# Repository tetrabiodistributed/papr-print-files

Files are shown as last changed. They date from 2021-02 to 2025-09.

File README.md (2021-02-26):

# papr-print-files
This repository contains all of the files necessary to print components of the Tetra PAPR.

Please see the documentation in https://tetrabiodistributed.github.io/papra/.

Please note that there is no warranty, real or implied, for those who build these devices on their own.  We simply cannot assure the quality of the work you've done.

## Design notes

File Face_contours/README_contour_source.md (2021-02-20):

# Contour Sourcing
-----------------

These contours were derived using NIOSH headforms, referenced below.  Once the headform had been loaded into Fusion 360, the following procedure was used to create the contours:

Beginning with the NIOSH large 3D headform, the initial design was created on a 2D plane using a B-spline for the inner profile, relative to the headform not using any explicit geometric relations. The spline positioning and shape was adjusted to mimic the coverage of existing FFRs. A copy of the profile was then projected 4 mm radially outward in the same plane to create the outer profile. These two B-splines were joined with vertical lines at either end to create a closed contour. The contour was projected from the 2D plane onto the 3D surface of the Large NIOSH Headform from the Principal Component Analysis Study, forming the face contact surface. The surface was then mirrored about the center plane.

## Additional references
---------------------

1. "Advanced Headforms for Evaluating Respirator Fit", Michael Bergman, MS; Ziqing Zhuang, PhD; Ronald E. Shaffer, PhD . July 25, 2013. Referenced from https://blogs.cdc.gov/niosh-science-blog/2013/07/25/headforms/ on Feb 13, 2021.

2. "NIOSH Anthropometric Data and ISO Digital Headforms" Updated on Updated April 23, 2020. NIOSH Dataset RD-10130-2020-0. Referenced from https://www.cdc.gov/niosh/data/datasets/rd-10130-2020-0/default.html on Feb 13, 2021.

3. Zhuang, Z.Q., B. Bradtmiller, and R.E. Shaffer: New respirator fit test panels representing the current US civilian work force. Journal of Occupational and Environmental Hygiene 4(9): 647-659 (2007).

4. Zhuang, Z., S. Benson, and D. Viscusi: Digital 3-D headforms with facial features representative of the current US workforce. Ergonomics 53(5): 661-671 (2010).

5. Hanson, D., R. Bergs, Y. Tadesse, V. White, and S. Priya: Enhancement of EAP Actuated Facial Expressions by Designed Chamber Geometry in Elastomers. Proc. SPIE’s Electroactive Polymer Actuators and Devices Conf., 10th Smart Structures and Materials Symposium, San Diego(2006).

6. Hanson, D., and V. White: Converging the Capabilities of ElectroActive Polymer Artificial Muscles and the Requirements of Bio-inspired Robotics. Smart Structures and Materials 2004: Electroactive Polymer Actuators and Devices (EAPAD), edited by Yoseph Bar-Cohen, Proceedings of SPIE Vol. 5385 (SPIE, Bellingham, WA), 2004.

7. Bergman, M., Z. Zhuang, R.J. Wande, D. Hanson, B. Heimbuch, M. McDonald et al.: Development of an Advanced Respirator Fit Test Headform. Journal of Occupational and Environmental Hygiene In Press(2013).

8. Zhuang, Z., M. Bergman, M. Joseph, and R. Shaffe: Human Correlation Fit Testing of a Static Advanced Headform. Presentation at the NPPTL Stakeholder Meeting on Respiratory Protection for Healthcare Workers, Atlanta, GA June 18, 2013 (2013).

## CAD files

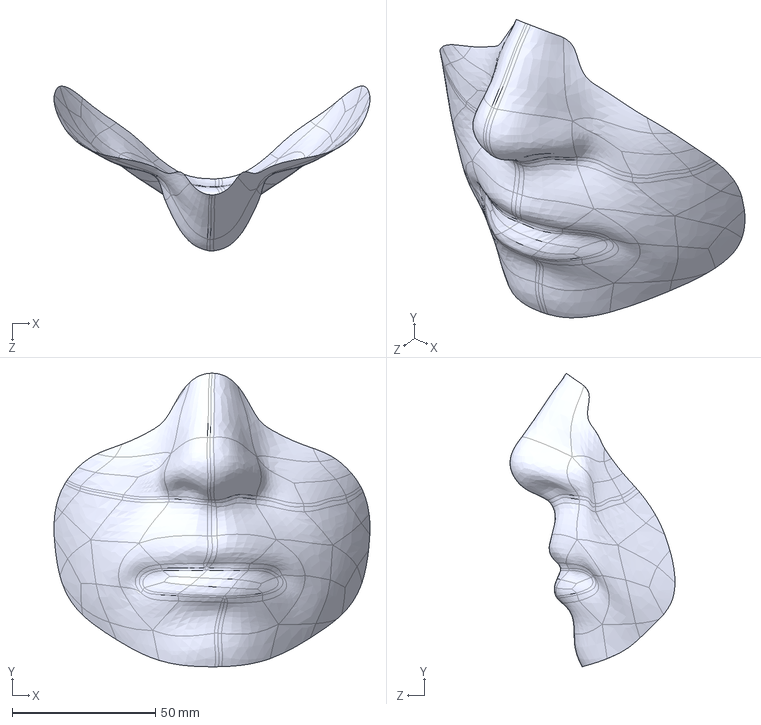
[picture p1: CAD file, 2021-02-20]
Face_contours/STEP/full_face/LRG_face_surface-full.STEP
110.4 x 102.5 x 57.6 mm

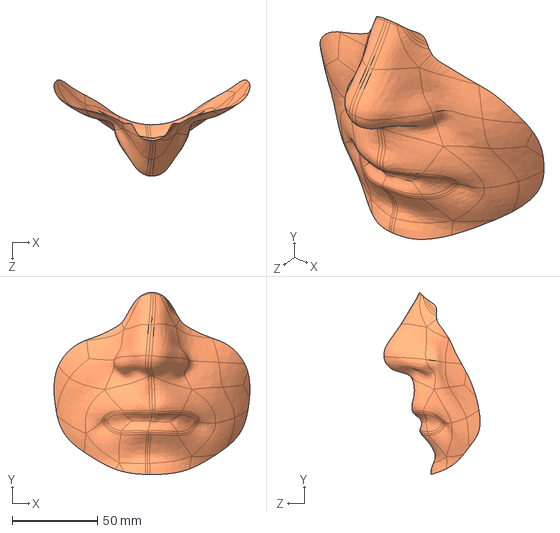
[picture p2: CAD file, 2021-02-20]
Face_contours/STEP/full_face/LRG_face_surface-full_5mm.STEP
115.0 x 106.8 x 56.5 mm

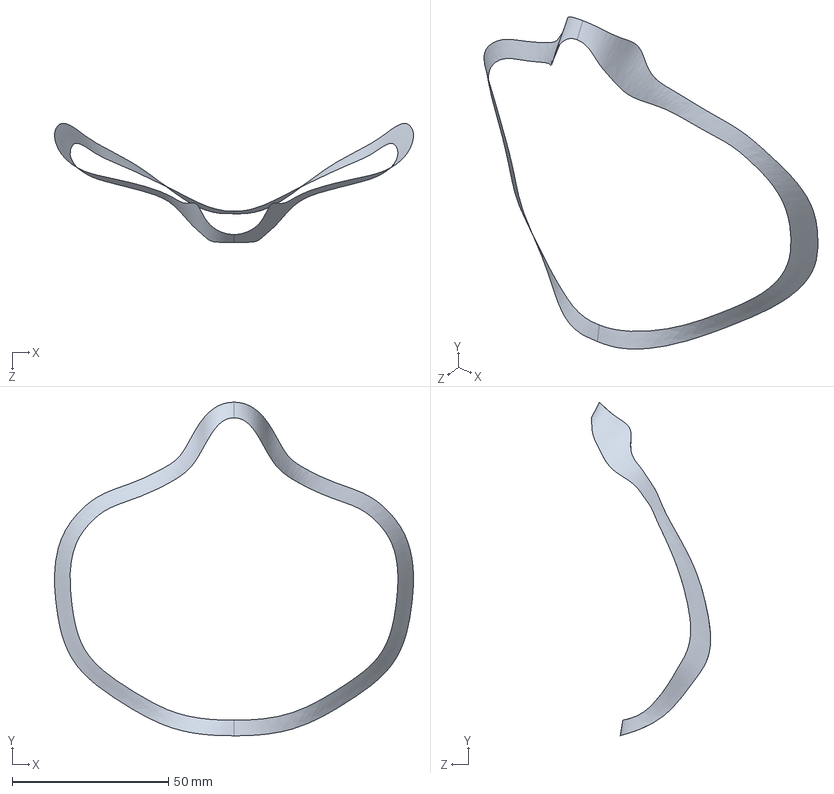
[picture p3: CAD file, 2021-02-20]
Face_contours/STEP/LRG_face_surface.STEP
114.9 x 106.8 x 38.2 mm

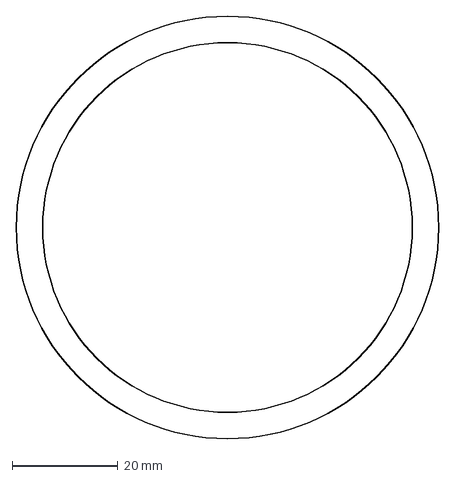
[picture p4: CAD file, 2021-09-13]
Gaskets/GermGuardian Filter PAPRa/P-TET-000121-1_Mask Gasket.dxf
80.0 x 80.0 mm

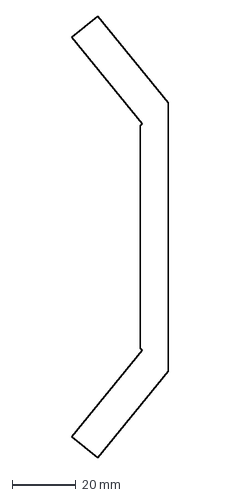
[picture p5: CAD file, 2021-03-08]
Gaskets/P-TET-000117-0 Funnel Gasket.dxf
30.2 x 138.2 mm

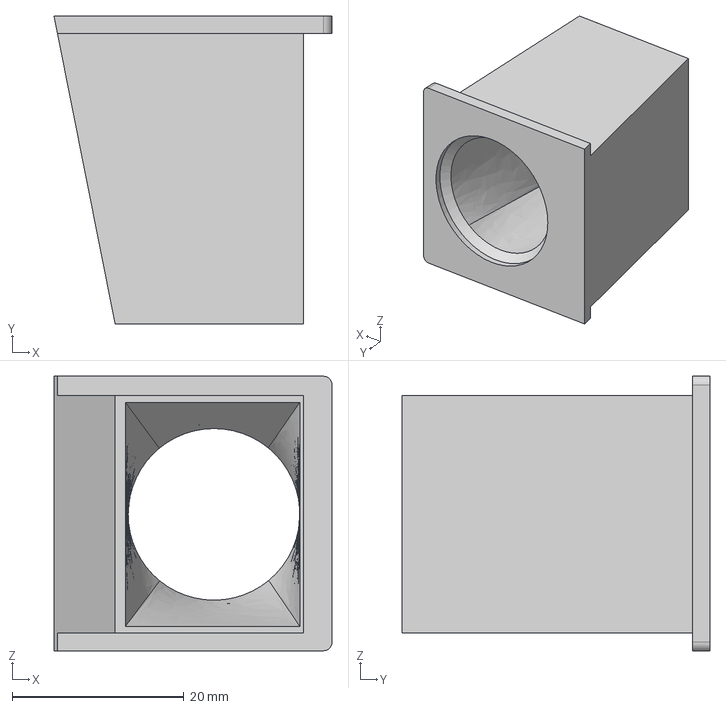
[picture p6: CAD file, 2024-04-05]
STEP/120mm Stealth Fan Box/P-TET-000179 Spout Interface.step
32.4 x 35.9 x 32.0 mm

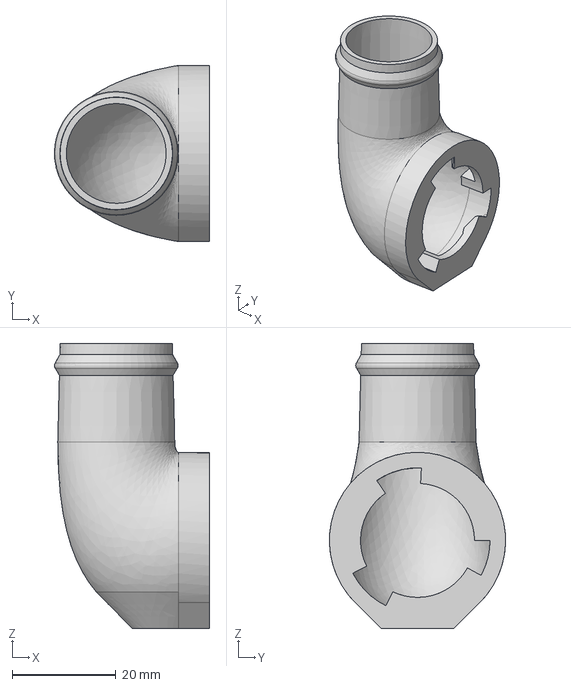
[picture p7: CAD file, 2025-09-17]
STEP/3M_Adapter/P-TET-000150 - 3M Right Angle Adapater.step
29.9 x 34.0 x 55.0 mm

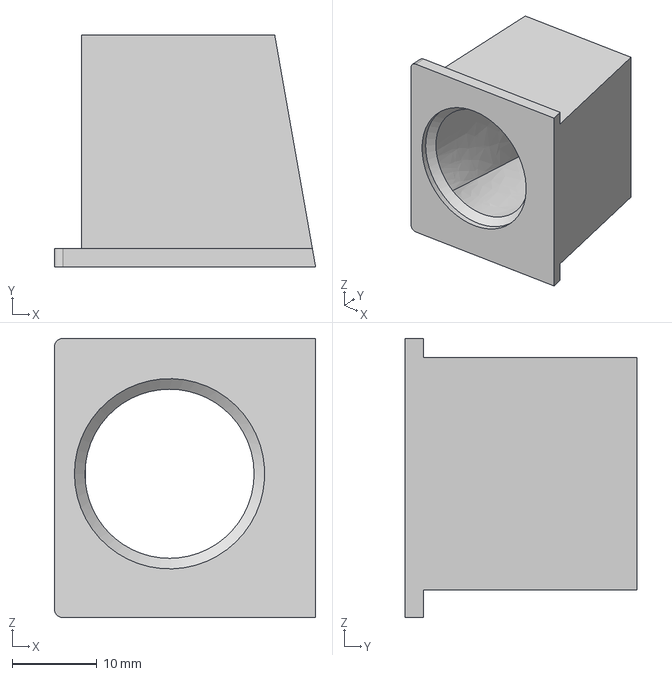
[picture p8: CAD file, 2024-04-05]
STEP/96mm Sanyo Fan Box/P-TET-000152 Spout Interface.step
30.9 x 27.5 x 33.0 mm

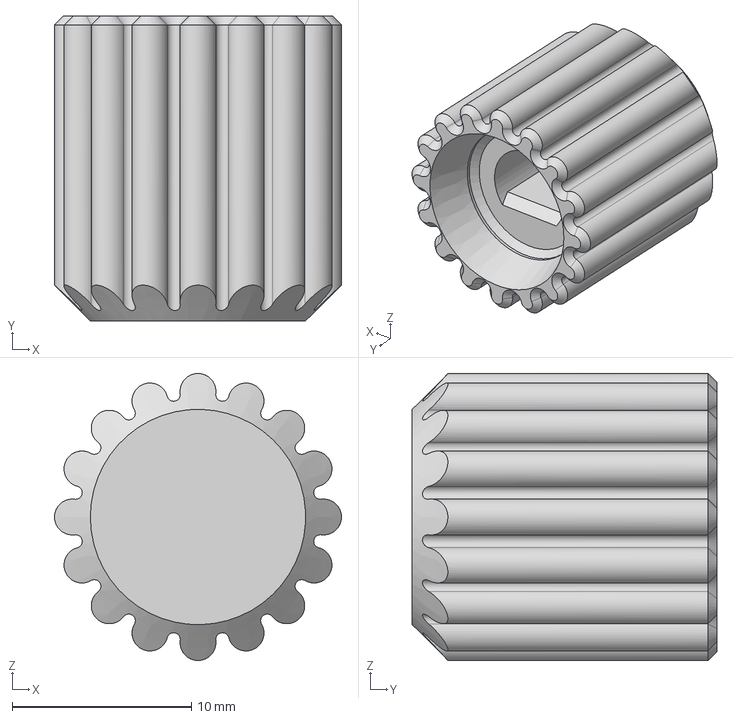
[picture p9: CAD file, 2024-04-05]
STEP/M12 Battery Housing/P-TET-000100 M12 Knob.step
16.0 x 17.0 x 16.0 mm

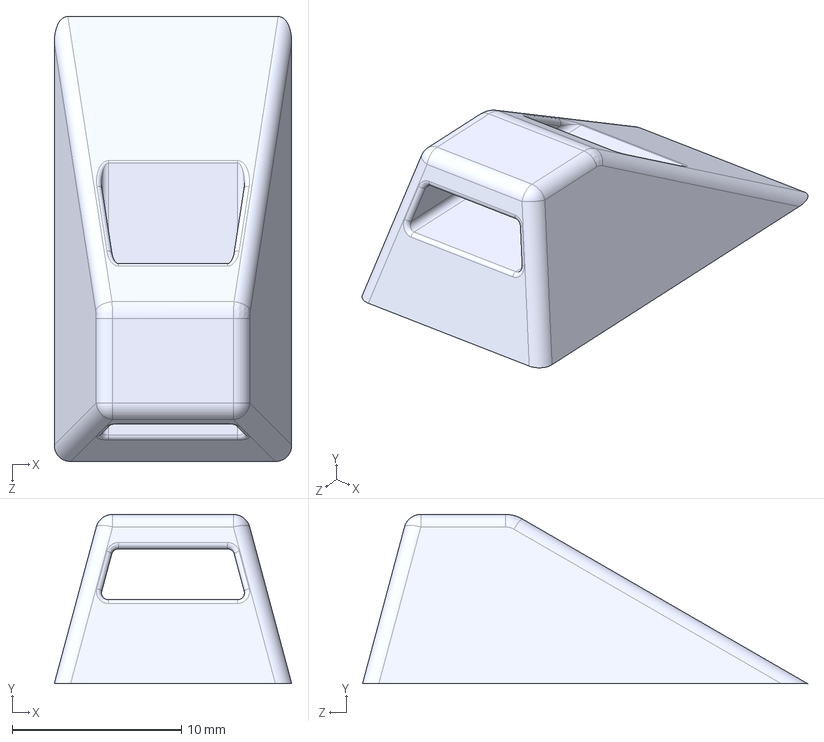
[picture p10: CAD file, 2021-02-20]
STEP/PAPR_strap_mounts/PAPR_facefit_strap_tie-points.STEP
14.0 x 10.00 x 26.3 mm

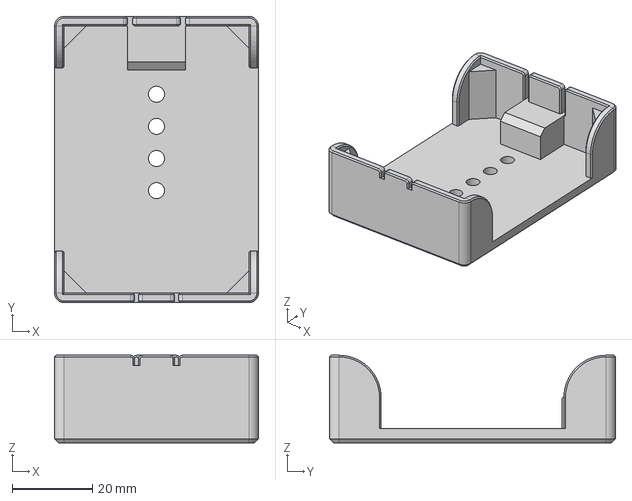
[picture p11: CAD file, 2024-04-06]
STEP/Tetra-PCB-jig-v3.1.step
50.8 x 71.3 x 21.8 mm

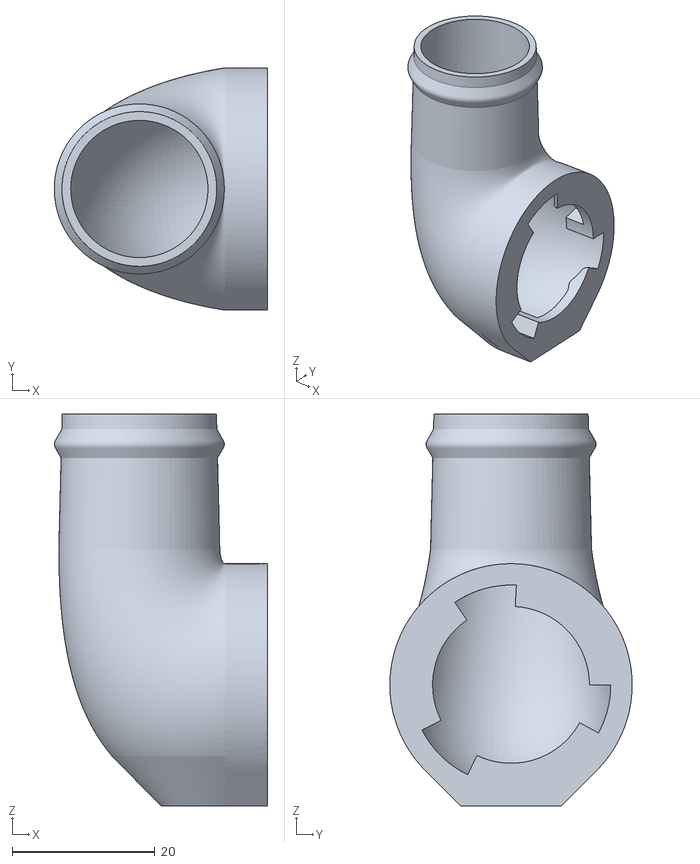
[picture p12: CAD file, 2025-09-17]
STLs/3M Adapter/P-TET-000150 - 3M Right Angle Adapater.stl
29.9 x 34.0 x 55.0

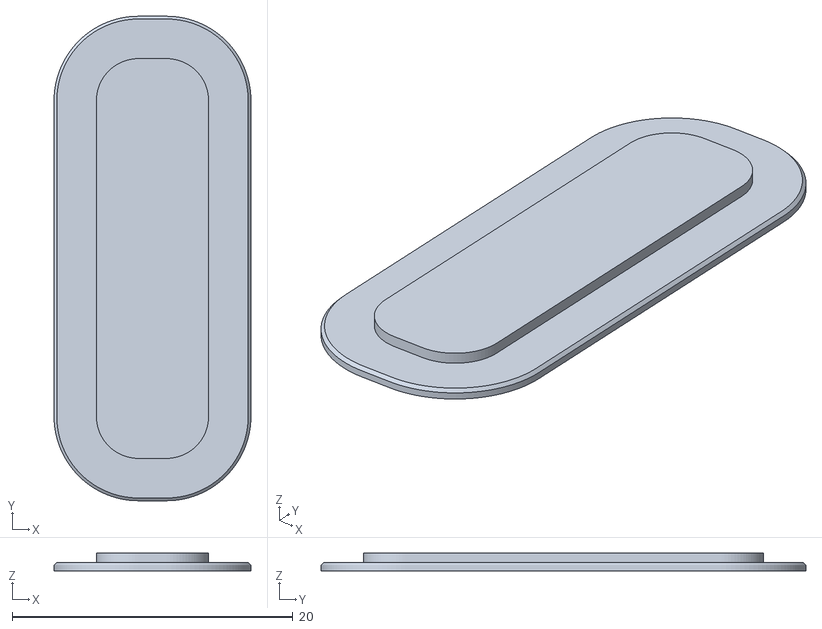
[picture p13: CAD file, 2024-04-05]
STLs/battery_controller/P-TET-000195 M12 Light Panel.stl
14.0 x 34.5 x 1.25

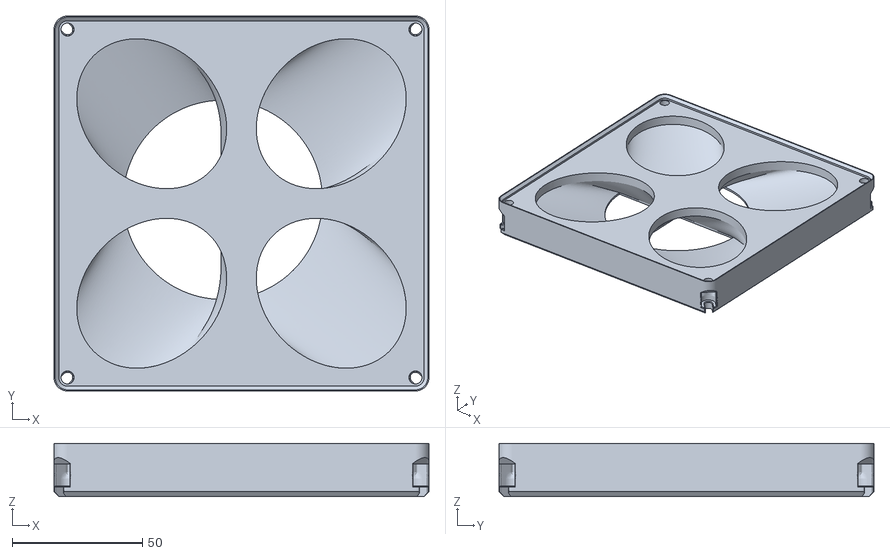
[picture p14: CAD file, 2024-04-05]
STLs/fan_box/120mm Stealth Parts/P-TET-000182 Stealth Filter Interface.stl
144.0 x 144.0 x 20.4

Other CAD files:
Face_contours/STEP/full_face/MED_face_surface-full.STEP
STLs/fan_box/96mm Stealth Parts/P-TET-000153 MOLLE Strap.stl
STLs/fan_box/GermGuardian Fan Box/P-TET-000133-4L_Weather_Guard.stl
STLs/m12_battery_controller_housing/P-TET-000169 - M12 Battery Back Plate.stl
Face_contours/DXF/LRG_face_surface.DXF
Face_contours/DXF/MED_face_surface.DXF
Face_contours/DXF/SML_face_surface.DXF
Face_contours/STEP/MED_face_surface.STEP
Face_contours/STEP/SML_face_surface.STEP
STEP/120mm Stealth Fan Box/P-TET-000175 Base.step
STEP/120mm Stealth Fan Box/P-TET-000176 MOLLE Catch.step
STEP/120mm Stealth Fan Box/P-TET-000177 MOLLE Strap.step
STEP/120mm Stealth Fan Box/P-TET-000178 Spacer.step
STEP/120mm Stealth Fan Box/P-TET-000180 Spout.step
STEP/120mm Stealth Fan Box/P-TET-000181 Stealth Filter Frame.step
STEP/120mm Stealth Fan Box/P-TET-000182 Stealth Filter Interface.step
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

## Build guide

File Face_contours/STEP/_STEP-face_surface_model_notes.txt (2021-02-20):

2021-02-06
Burhan Qaddoumi

***offset from interior contour (of 2D sketch)***

- LRG_face_surface.STEP = 5mm offset from interior contour
- MED_face_surface-full.STEP = 5mm offset from interior contour
- SML_face_surface-full.STEP = 5mm offset from interior contour

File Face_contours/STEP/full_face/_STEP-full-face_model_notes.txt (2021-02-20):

2021-02-06
Burhan Qaddoumi

***offset from interior contour (of 2D sketch)***

- LRG_face_surface-full.STEP = 4mm offset from interior contour (smaller overall area)
- LRG_face_surface-full_5mm.STEP = 5mm offset from interior contour
- MED_face_surface-full.STEP = 5mm offset from interior contour
- SML_face_surface-full.STEP = 5mm offset from interior contour

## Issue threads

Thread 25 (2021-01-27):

tetrabiodistributed/papr-print-files #25: Respirator without hose exploded diagram

mmroden, 2021-01-27:
Need a diagram without the hose exploded diagram

mmroden, 2021-01-27:
https://tetrabiodistributed.github.io/project-tetra-docs/papra-build-guide/components/building-tetra-papr-fan-box-v1/

mmroden, 2021-01-27:
https://tetrabiodistributed.github.io/project-tetra-docs/papra-build-guide/components/building-tetra-papr-mask-v1/  but without the hose, with the pressure lock

mmroden, 2021-02-17:
fusion file created with all the components, Darragh hasn't started with the exploded diagram yet

darraghbr, 2021-02-17:
Made a start, need to get access to the PAPRA part register to assign some part numbers in order to continue. @mechatroniks-git 
[D-TET-0-0 Mask Assembly Drawing.pdf](https://github.com/tetrabiodistributed/papr-print-files/files/5998623/D-TET-0-0.Mask.Assembly.Drawing.pdf)

mmroden, 2021-02-17:
The mount goes into the mask; the mask has to be deformed to get the mount onto it.  Like so: [https://photos.smugmug.com/Tetra-Testing/Tetra-PAPRa-Build-Party-31-Jan-2021/i-VdMFNk7/0/1fce67c4/X2/_MMR0595-X2.jpg](image)

mmroden, 2021-02-17:
note also that there are tabs for the mount to fit onto the mask itself

darraghbr, 2021-02-20:
[D-TET-001104-0 Mask Assembly Drawing.pdf](https://github.com/tetrabiodistributed/papr-print-files/files/6016745/D-TET-001104-0.Mask.Assembly.Drawing.pdf)

mmroden, 2021-02-20:
You're going to hate me, but I forgot to say that we need some filter material in there.  It goes between the gasket (3) and the front element (4) (right, @DHHwangPhD ?).  We've been using material cut from 3-layer surgical masks, which still provides N95 levels of protection

darraghbr, 2021-02-20:
No worries, updated here

[D-TET-001104-0 Mask Assembly Drawing.pdf](https://github.com/tetrabiodistributed/papr-print-files/files/6016808/D-TET-001104-0.Mask.Assembly.Drawing.pdf)

mmroden, 2021-02-20:
lgtm

closed 2021-02-20 by mmroden

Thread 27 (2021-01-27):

tetrabiodistributed/papr-print-files #27: Exploded diagram for the fan box for the Jan 2021 version of the PAPRa

mmroden, 2021-01-27:
Need an exploded diagram of the fan box

mmroden, 2021-01-27:
https://tetrabiodistributed.github.io/project-tetra-docs/papra-build-guide/components/building-tetra-papr-fan-box-v1/

darraghbr, 2021-02-10:
@mechatroniks-git @DHHwangPhD 

[image]

When I tried to add the fan box PCB I got some clipping issues when I put it where I expect it to go. I am using the file in git called TypeA_PAPR2.

mmroden, 2021-02-11:
the fan is upside down in this rendering, needs to be fitted

darraghbr, 2021-02-11:
Turns out I was looking at the wrong version. Version to use is V4.2.

darraghbr, 2021-02-17:
I've generated a milestone in Fusion. In Tetra PAPR\Archive\PAPRA V4\SinglePAPRv4 I've labelled it 'January version' is this the correct version of the assembly that was made in January? @DHHwangPhD  @mmroden

mmroden, 2021-02-17:
that's the one from Jan 6th, so it could do in a pinch.  The next version used these parts: 
[image], which looks like it might be model 4.1 with the most recent top plate and a base plate missing

darraghbr, 2021-02-17:
Are there still supports on the fan box outlet? I can't find a part that looks like that in any of the versions.

mmroden, 2021-02-17:
Check the funnel in the part you mentioned: Tetra PAPR\Archive\PAPRA V4\SinglePAPRv4

[image]

That would require supports

darraghbr, 2021-02-17:
Yep that's all fine, I'm just trying to make sure I use the right version.

mmroden, 2021-02-17:
gotcha.  I think the one we built had a part number on it, so it's not the one in that diagram; I think it's the same thing but with a part number.

mmroden, 2021-02-24:
not really necessary for the milestone

darraghbr, 2021-03-04:
solved in #82 ?

mmroden, 2021-03-12:
No bandwidth, won't do

closed 2021-03-12 by mmroden

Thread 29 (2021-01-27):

tetrabiodistributed/papr-print-files #29: exploded diagram of the v2 of the m12 battery controller

mmroden, 2021-01-27:
For these instructions:
https://tetrabiodistributed.github.io/project-tetra-docs/papra-build-guide/components/building-tetra-papr-m12-v2/

mechatroniks-git, 2021-01-27:
Is this along the lines of what you want?
[image]

mmroden, 2021-01-27:
That would be great!  If we had the ability to label the various bits, that
would be an extra awesome step, but I realize that may be a bridge too far

mechatroniks-git, 2021-01-27:
Or this? And image or pdf?

[image]

mmroden, 2021-01-27:
The second one is better; are the nuts not labeled because they are part of another part?

Image is great, pdf is a great addition, but image is the main deliverable I think.  PNG ideally, no jpg.

mechatroniks-git, 2021-01-27:
Ok, the parts are grouped in assemblies, so you only get 1 number for the assembly, might be a way to do multi-level as a flat assembly, but will get all the board level parts. In any case, there is lots of cleanup to do on the files to have a part list that is correct. This will take some time.

mmroden, 2021-01-27:
We probably need to do this for proper manufacturing handoff, I'd think.

mechatroniks-git, 2021-01-28:
Yes, lots of busy work getting this done right. Assigning part numbers, updating each part's material property and part #, then the part's list will be good for exploded view drawings.

darraghbr, 2021-02-10:
[A-TET-001102-0 M12 PAPRA Controller Drawing.pdf](https://github.com/tetrabiodistributed/papr-print-files/files/5961147/A-TET-001102-0.M12.PAPRA.Controller.Drawing.pdf)

Should be good to go @mmroden

mmroden, 2021-02-12:
Perfect, got the fixed lid in there too!

closed 2021-02-12 by mmroden

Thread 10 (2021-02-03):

### ISSUE TITLE
Facemask (08JAN20212) air is directed onto face

### ISSUE THREAD

**Issue by mechatroniks-git** [tetrabiodistributed/papr-print-files#10]
Nose gets really cold and chapstick is required for lips

**Comment by mmroden** [comment]
Closed by #31 with the grommet
![Screen Shot 2021-02-03 at 9 44 08 AM](https://user-images.githubusercontent.com/116251/106787302-67a98f80-6604-11eb-9c59-9a2f3a9429eb.png)

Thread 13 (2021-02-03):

### ISSUE TITLE
PCB connector placement in M12 Controller Body and Controller Plate can be off

### ISSUE THREAD

**Issue by mechatroniks-git** [tetrabiodistributed/papr-print-files#13]
Due to tolerances of the assembly (without a soldering fixture), connectors don't easily fit in housing

**Comment by mechatroniks-git** [comment]
@DHHwangPhD I would recommend slotting the DC power jacks to allow for board misalignment. Slotting it by 1mm total (.5mm left to right) should be sufficient and still be covered by the washer & nut. 

![image](https://user-images.githubusercontent.com/57600622/105612138-ebdf5580-5d6e-11eb-8595-10ab72b035c8.png)

![image](https://user-images.githubusercontent.com/57600622/105612166-25b05c00-5d6f-11eb-808f-4bdf32b331ca.png)

**Comment by DHHwangPhD** [comment]
Done in v18 of the M12 PAPRA Controller

**Comment by mmroden** [comment]
![image (23)](https://user-images.githubusercontent.com/116251/106786294-3da39d80-6603-11eb-92af-1b831b5ccdbc.png)
Solved in #31 with updated holes on the bottom of the controller, as well as with the updated lid
![image (24)](https://user-images.githubusercontent.com/116251/106786357-501dd700-6603-11eb-81e5-c910e5ffef43.png)

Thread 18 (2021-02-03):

### ISSUE TITLE
Ninjaflex mask ("FitMaskBody.stl") has an internal lip that is a bit sharp

### ISSUE THREAD

**Issue by mmroden** [tetrabiodistributed/papr-print-files#18]
![Image from iOS (2)](https://user-images.githubusercontent.com/116251/105079782-c2f45300-5a44-11eb-9e04-afff3df0c84a.jpg)
This internal lip is a bit sharp and prone to printing errors when printed with supports (which have to be used)

![Image from iOS (3)](https://user-images.githubusercontent.com/116251/105079825-d69fb980-5a44-11eb-812a-1d6ea4f8013b.jpg)
This rip comes from the Prusa slicer supports being removed

**Comment by Burhan-Q** [comment]
Cross section view of mask at the highest point of the nose region
![image](https://user-images.githubusercontent.com/62214284/105610557-2b616e00-5d7e-11eb-8a93-9da974bce0ac.png)

**Comment by mmroden** [comment]
the image of my cut-up face
![Uploading Image from iOS (3).jpg…]()

**Comment by mmroden** [comment]
Solved from #31 
![Image from iOS (5)](https://user-images.githubusercontent.com/116251/106786753-c4587a80-6603-11eb-894d-6b242aa037f4.jpg)

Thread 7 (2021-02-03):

### ISSUE TITLE
Light pipes not captured, can fall off

### ISSUE THREAD

**Issue by mechatroniks-git** [tetrabiodistributed/papr-print-files#7]
Light pipe is not fully secured to it's position and can fall out of the PCB

**Comment by mechatroniks-git** [comment]
@DHHwangPhD This looks good, not sure if you tested it, but might be better if you cheated the tab closer to the PCB, perhaps flush with the lower section?

![image](https://user-images.githubusercontent.com/57600622/105612539-bb4ceb00-5d71-11eb-8f43-2496ada45c8d.png)

**Comment by mmroden** [comment]
How will this get inserted?  The pressure fit is already tight, I'd be
worried about some alignment problem when it jams into place.

**Comment by DHHwangPhD** [comment]
![image](https://user-images.githubusercontent.com/68876187/105811968-3c6ad480-5f62-11eb-8294-bdf75ce56fdb.png)

Trying a clip style light pipe holder.

**Comment by mmroden** [comment]
![image (22)](https://user-images.githubusercontent.com/116251/106785854-bce4a180-6602-11eb-8f5b-66460ba1d590.png)
Closed by #31

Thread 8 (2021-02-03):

### ISSUE TITLE
M12 connector holes undersized

### ISSUE THREAD

**Issue by mechatroniks-git** [tetrabiodistributed/papr-print-files#8]
The holes for the DC power jacks and the on/off knob are undersized

**Comment by mechatroniks-git** [comment]
@DHHwangPhD  For standard part hole clearances in CNC, the following is a good guide:https://www.datametal.com/wp-content/uploads/2018/03/Metric-Tap-and-Clearance-Drill-Sizes.pdf

For CNC, you can get away with close-fit on holes, but for 3D printing, I wouldn't go tighter than standard fit. So the knob should be 7.7mm and the DC jacks should be 8.8mm (but also slotted left to right by +/-0.5mm).

![image](https://user-images.githubusercontent.com/57600622/105613158-c6097f00-5d75-11eb-81a5-eaea3b6c2c22.png)

![image](https://user-images.githubusercontent.com/57600622/105613151-af632800-5d75-11eb-9394-962172d94f0a.png)

**Comment by DHHwangPhD** [comment]
Updated the holes with 7.7 and 8.8 slots

**Comment by mmroden** [comment]
![image (23)](https://user-images.githubusercontent.com/116251/106786062-fae1c580-6602-11eb-8c0a-78597bd84b91.png)
closed by #31

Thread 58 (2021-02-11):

tetrabiodistributed/papr-print-files #58: part registry

mmroden, 2021-02-11:
need a central part registry for all tetra parts
should be its own repo
comfortable for just being a google sheet
change history for adding new parts (should be a google sheet)
should have proper access control

P-TET exists
A-TET assemblies
D-TET drawings

Should be its own thing, just recording this hear

mechatroniks-git, 2021-02-11:
Currently we've been using:

```
A-TET-ZZZZZZ-R = Assembly 
    ZZZZZZ-R is Assembly Number & Revision
P-TET-ZZZZZZ-R = Part
    ZZZZZZ-R is Part Number & Revision
M-YYY-ZZZZZ = Buy Part, M = Manufacturer, YYY = manufacturer code (ex, UNI = Unistrut)
    ZZZZZ = Manufacturer part number
V-XXX-ZZZZZ = OTS part, V = Vendor, XXX = vendor code (ex, MCM = McMaster-Carr)
    ZZZZ = Vendor part number 
```

darraghbr, 2021-02-11:
So I envision the solution to this being a form.

This form should have 4 tick boxes to specify whether you want to request a part, assembly, drawing or document number.

A field to accept a string with the name of the part or assembly or drawing etc.

Another field to accept a string with the name of the requester. 

Upon submission the form should return the next unused part, assembly, drawing etc number.

mechatroniks-git, 2021-02-11:
Currently found part #s here: 
https://docs.google.com/spreadsheets/d/1nCw9LUN7ygv8B8hno6poN-m15rsixNSolVTXhXynrfw/edit?pli=1#gid=0
https://docs.google.com/spreadsheets/d/1SvVoTHTWQuhzA31efnyqhaFsMOlKPyU90ATQrHQNn1k/edit#gid=0

darraghbr, 2021-02-13:
I have prototyped a system to issue numbers using something called Appsheet that uses a google sheet in the background, needs to be paid if we want to deploy it. I am investigating funding at the moment. 

This solution is pretty quick and dirty, I think that if multiple people were requesting the same thing at the same time it would probably break a bit.

I think we should also issue document numbers that can then get thrown into a document register. What designation should we use for documents?

Currently I have P-TET for parts, A-TET for assemblies, D-TET for drawings.

capsulecorplab, 2021-02-14:
I think this issue falls under a bigger discussion of how we internally facilitate product lifecycle management (PLM) for an open-source hardware (OSHW) project. I would be cautious of jumping the gun on using a service that requires a paywall, as those generally tend to contradict the principles of OSHW.

darraghbr, 2021-02-14:
It would be absolutely nothing more than a stop gap measure. 

While the service does require funding the only way we would lose the data is if the google sheet (which is currently in my personal account but can be moved) were lost for some reason.

mmroden, 2021-02-20:
@mechatroniks-git created a new repo for part numbers: https://github.com/tetrabiodistributed/tetraPLM

closed 2021-02-20 by mmroden

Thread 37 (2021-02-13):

### ISSUE TITLE
P-TET-000112-0 DC Jack hole size too small

### ISSUE THREAD

**Issue by mechatroniks-git** [tetrabiodistributed/papr-print-files#37]
Diameter too small for jack, open up to 8.4mm

![image](https://user-images.githubusercontent.com/57600622/106397441-51ac8c80-63c2-11eb-9e29-0758db7fc0a2.png)

**Comment by mmroden** [comment]
Should be fixed in the latest box, will put in a PR with the new fan box assembly

**Comment by mmroden** [comment]
Part of this work 
![image (25)](https://user-images.githubusercontent.com/116251/106787525-aa6b6780-6604-11eb-900a-4af71b76577f.png)

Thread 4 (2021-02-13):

### ISSUE TITLE
Funnel into lower box

### ISSUE THREAD

**Issue by mechatroniks-git** [tetrabiodistributed/papr-print-files#4]
Difficult to mate funnel to box, fit is tight on PLA prints. 

Recommend adding chamfer lead edge & increase fit clearance.

**Comment by DHHwangPhD** [comment]
Edge has been chamfered.

**Comment by mmroden** [comment]
Part of this work, needs to be tested: 
![image (25)](https://user-images.githubusercontent.com/116251/106787576-ba834700-6604-11eb-96bf-1023ef957ed3.png)

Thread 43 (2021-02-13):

### ISSUE TITLE
m12 controller knob didn't fit

### ISSUE THREAD

**Issue by mmroden** [tetrabiodistributed/papr-print-files#43]
The current controller knob didn't fit the potentiometer, could be a printer or material difference

**Comment by mechatroniks-git** [comment]
Print is good with PETG on Makerbot Rep 2. 

Issue can be fixed by printing at increased scale, adjust per printer 1-2% should suffice, part should work without problem with scaling +/-5% as the only critical feature is the 6mm knob shaft.

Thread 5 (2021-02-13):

### ISSUE TITLE
Funnel fit into box

### ISSUE THREAD

**Issue by mechatroniks-git** [tetrabiodistributed/papr-print-files#5]
Funnel can be installed in 2 positions, only one way is correct.

**Comment by mmroden** [comment]
Prevented by the board being placed into the fan box
![image (25)](https://user-images.githubusercontent.com/116251/106787800-ff0ee280-6604-11eb-8932-d123bd7c8d91.png)

**Comment by mmroden** [comment]
Not yet tested, can't close yet

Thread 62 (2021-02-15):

tetrabiodistributed/papr-print-files #62: Create A4/Letter versions of the gaskets

mmroden, 2021-02-15:
There is currently only an A3 template for the gaskets

darraghbr, 2021-02-17:
Made a letter version, the question I have is should I resize the drawing box so that it all fits on one row or is what I have done fine? @mmroden 

[Tetra Papr Drawing Template A v2.pdf](https://github.com/tetrabiodistributed/papr-print-files/files/5998632/Tetra.Papr.Drawing.Template.A.v2.pdf)

mmroden, 2021-02-17:
What do you mean by "it all fits on one row"?  I'm not sure the ramifications of that decision

darraghbr, 2021-02-17:
Well if you look at the pdf I've uploaded, the section with the 3rd angle projection symbol, the tolerances and units are in their own little box above the main drawing box, whereas in the D size version all of that info is in one box at the bottom right of the page. 

It's purely a stylistic thing and if you don't mind the way it looks I will continue.

mmroden, 2021-02-17:
I do not mind the way it looks at all.

The way @DHHwangPhD had his gaskets cut by his cricut, he had them one inside of the other to save material-- can that be reflected here?  Or is that a different kind of concern?

darraghbr, 2021-02-17:
If we are also uploading .dxf files for all of the gaskets that is up to the end user. It is entirely possibly to nest them inside one another.

mmroden, 2021-02-17:
works for me, we are definitely uploading dxf files to the gaskets folder here

darraghbr, 2021-02-22:
I've finished the letter sized versions of these drawings.

mmroden, 2021-02-22:
Maybe a PR if they're not in the appropriate directory?

darraghbr, 2021-02-22:
They're in #69

mmroden, 2021-03-03:
Merged

closed 2021-03-03 by mmroden

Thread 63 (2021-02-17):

tetrabiodistributed/papr-print-files #63: Exploded diagram for the Feb 2021 fan box

mmroden, 2021-02-17:
now with the gasket for the funnel instead of the snap to fit

darraghbr, 2021-02-17:
I tried to get the view from the other side but to no avail. I need an assembly number for this set up as well @mechatroniks-git 

[D-TET-0-0 Fan Box Drawing.pdf](https://github.com/tetrabiodistributed/papr-print-files/files/5998568/D-TET-0-0.Fan.Box.Drawing.pdf)

mechatroniks-git, 2021-02-20:
Updates to parts list:
[image]

I prefer using tangent edges, shortened on the view
[image]

darraghbr, 2021-02-20:
Thanks Patrick, I have addressed your comments and given it an assembly number in this version.

[D-TET-001103-0 Fan Box Drawing.pdf](https://github.com/tetrabiodistributed/papr-print-files/files/6016193/D-TET-001103-0.Fan.Box.Drawing.pdf)

mmroden, 2021-02-20:
Hole placement for the new fan controller board will likely need to be updated, but!  This is sufficient for assembly

closed 2021-02-20 by mmroden

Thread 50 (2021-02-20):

### ISSUE TITLE
create mounting points as a separate STEP file

### ISSUE THREAD

**Issue by mmroden** [tetrabiodistributed/papr-print-files#50]
the current mask (as of Feb 2021) with all the mounting points as separate bodies in the STEP file

**Comment by Burhan-Q** [comment]
@mmroden I don't have the mask with the filter mount that @DHHwangPhD made, so I don't have a way to upload that. The mounting points STEP file has been added to PR #60

**Comment by Burhan-Q** [comment]
@DHHwangPhD to added mask file

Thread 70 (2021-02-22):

tetrabiodistributed/papr-print-files #70: Generate ISO standard drawing templates

darraghbr, 2021-02-22:
I've generated some drawing templates that fit the ISO standard so we can issue drawings under that standard.

@mmroden please review when able.

[Tetra A4 Drawing Template.pdf](https://github.com/tetrabiodistributed/papr-print-files/files/6025045/Tetra.A4.Drawing.Template.pdf)
[Tetra A3 Drawing Template.pdf](https://github.com/tetrabiodistributed/papr-print-files/files/6025046/Tetra.A3.Drawing.Template.pdf)

mmroden, 2021-02-22:
These LGTM, but I would ask @mechatroniks-git what he thinks, since this is my first real rodeo with mechanical drawings

mechatroniks-git, 2021-02-22:
Looks good. We had planned on making templates for assembly and part drawings. With an additional part drawing template specifically for 3D printed parts. Not sure we need all those, but the assembly comment makes the template destined for assembly drawings.

closed 2021-03-01 by capsulecorplab

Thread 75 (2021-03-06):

### ISSUE TITLE
Orient STLs for proper printing

### ISSUE THREAD

**Issue by mmroden** [tetrabiodistributed/papr-print-files#75]
Orient STLs so zero plane is print plane; right now, they are all over the place

**Comment by mmroden** [comment]
#74 gets us closer

**Comment by mechatroniks-git** [comment]
https://forums.autodesk.com/t5/fusion-360-design-validate/stl-exported-sideways/td-p/6718459

**Comment by mmroden** [comment]
To be done: respirator parts, fan box parts.  m12 is done from #74

**Comment by mmroden** [comment]
fan box cover (hex top) is not oriented properly

**Comment by mmroden** [comment]
fixed by #88 for mask and fan box

**Comment by mmroden** [comment]
Solved

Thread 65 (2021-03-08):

### ISSUE TITLE
Update the fan box for the new fan box power/controller board

### ISSUE THREAD

**Issue by mmroden** [tetrabiodistributed/papr-print-files#65]
The fan power board with the airtight seal to the outside is a different part, need to update the box

**Comment by mechatroniks-git** [comment]
Ordered 3 each from OshPark to verify design changes. Expect boards back by March 13th (estimated, not a firm date). Will need to also order PCB parts to assemble board.

![image](https://user-images.githubusercontent.com/57600622/109043934-ab813900-7686-11eb-8837-74beba8fc467.png)

**Comment by mechatroniks-git** [comment]
@mmroden This delivery schedule will push the milestone date out to mid-March

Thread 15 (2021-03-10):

### ISSUE TITLE
Make a BOM

### ISSUE THREAD

**Issue by mechatroniks-git** [tetrabiodistributed/papr-print-files#15]

**Comment by mechatroniks-git** [comment]
See: https://docs.google.com/spreadsheets/d/1SvVoTHTWQuhzA31efnyqhaFsMOlKPyU90ATQrHQNn1k/edit#gid=0

**Comment by mmroden** [comment]
Stuff at the bottom is not defined, respirator needs part numbers

**Comment by mmroden** [comment]
Have one for the 29 Jan version, need a copy to be for the next build party

**Comment by mechatroniks-git** [comment]
@Burhan-Q can you assign part numbers to the respirator parts? I setup https://github.com/tetrabiodistributed/tetraPLM so anyone can create a new part number

**Comment by Burhan-Q** [comment]
Reserved for respirator components:

P-TET-000-118-0
P-TET-000-119-0
P-TET-000-120-0
P-TET-000-121-0
P-TET-000-122-0

**Comment by mmroden** [comment]
webbing and triglides need to get finished

**Comment by mechatroniks-git** [comment]
BOM created, waiting on PR merge - https://github.com/tetrabiodistributed/tetraPLM/pull/2

**Comment by mmroden** [comment]
reached out to @sharpybynature to see if we can get Helpful help here

**Comment by mmroden** [comment]
https://erpnext.com/open-source-manufacturing-erp-software

**Comment by mechatroniks-git** [comment]
We need to install it on our own git https://github.com/frappe/erpnext

**Comment by DHHwangPhD** [comment]
@mechatroniks-git @mmroden @darraghbr @capsulecorplab  BOM spreadsheet is incorrect on the parts that need to be printed. M12 parts are older models. Needs updating. Will bring up at Saturday meeting.

**Comment by mmroden** [comment]
BOM was updated

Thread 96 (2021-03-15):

tetrabiodistributed/papr-print-files #96: Fan box jack issues

DHHwangPhD, 2021-03-15:
Problems with the power jack in the fan box.
Original power jack for the board is not sealed.
New power jack is sealed, but will require custom cables.
Other jacks like M12 have been discussed with @mechatroniks-git

darraghbr, 2021-03-15:
Can you expand on why you think the new connector needs a custom cable? The jack is for a standard 5.5 mm x 2 mm plug.

mechatroniks-git, 2021-03-15:
The connector entry is deeper and has an oring seal, so the cable end needs to be longer and match the diameter at the seal

mmroden, 2021-03-15:
yeah @darraghbr-- @mechatroniks-git had to sand down a connector to make a custom connector for a cable.  So either we need another jack or we need custom cables.

darraghbr, 2021-03-15:
By the looks of things the compatible jack uses a thread to pull the 2 parts together to create a seal.

https://www.mouser.co.uk/ProductDetail/Switchcraft/S761KS15?qs=fbkhFuCHoTam5cvHIFHKsw%3D%3D

mechatroniks-git, 2021-03-19:
[image]
BNC Cable: https://www.monoprice.com/product?p_id=16180
BNC Connector: https://www.digikey.com/en/products/detail/adam-tech/RF1-01A-D-00-75-M/9831054

mmroden, 2021-03-20:
Will likely close if the BNC connector route works: #102

closed 2021-05-13 by mmroden

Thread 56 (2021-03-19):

### ISSUE TITLE
DC Jack on fan box is not sealed

### ISSUE THREAD

**Issue by mechatroniks-git** [tetrabiodistributed/papr-print-files#56]
CUI DC Jack allows air to leak. Consider options for sealed unit.

Switchcraft L722RAS is IP68 rated, costs ~$5. Would require a board spin and bigger hole in the fan box.

![image](https://user-images.githubusercontent.com/57600622/107534002-5b798100-6b74-11eb-8442-e672dfb6d083.png)

**Comment by mechatroniks-git** [comment]
Straight version cheaper at newark: https://www.newark.com/switchcraft-conxall/pcl722as/connector-power-entry-jack-5a/dp/81R0092?CMP=AFC-OP

**Comment by mechatroniks-git** [comment]
@mmroden @DHHwangPhD I need to know if this is something I should proceed with. Do we need IP rated connectors? Should we look at something cheaper like this, that can be easier to seal (washer gasket and hot glue/silicone on the back)? https://www.newark.com/cliff-electronic-components/fc681473/dc-power-jack-1a-12vdc-panel/dp/08X1631

**Comment by mechatroniks-git** [comment]
Here is the L722RAS on existing PCB. Changes required
1. new PCB footprint
2. connector center height relative to PCB is taller, so to keep PCB in same location, hole on box moves 1.483mm. Also diameter increases to 11.8mm (was 8.8mm)

![image](https://user-images.githubusercontent.com/57600622/107683903-fe0a3080-6c56-11eb-9da4-7f9db21908a3.png)

**Comment by mmroden** [comment]
It is now sealed!

Testing two jan 9 units, n99 pass levels are:
1. 70
2. 80

Testing one Jan 31 unit, n99 pass level is:
1. 400

Testing three 13 March 2021 n99 pass levels:
1. 850  (24 particles)
2. 700 (30 particles)
3. 1200 (15 particles)
22k particles-- at these ratios, the numbers change a lot when a single particle is added or subtracted

But the new boxes are markedly better than the old

We do need better test hoses

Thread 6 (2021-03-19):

### ISSUE TITLE
Base plate bowing

### ISSUE THREAD

**Issue by mechatroniks-git** [tetrabiodistributed/papr-print-files#6]
When assembled, base plate exhibits bowing in the middle of the plate

**Comment by mmroden** [comment]
Fan is not actually at spec properly, will test things to solve the bowing-- contrary to the drawings, there's a .5mm change possible in the actual fan.

**Comment by mmroden** [comment]
@DHHwangPhD is looking this over

**Comment by mmroden** [comment]
Considered solved with the new molle plate

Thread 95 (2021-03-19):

### ISSUE TITLE
Adapter for different size jack holes in the fan box

### ISSUE THREAD

**Issue by DHHwangPhD** [tetrabiodistributed/papr-print-files#95]
Previous non IP rated jack is smaller than the sealed jack. The sealed jack is larger. Need an adapter that reduces the hole size so the current fan box can use the older board/jack.

**Comment by DHHwangPhD** [comment]
Stopgap plan.

**Comment by DHHwangPhD** [comment]
We need this to make the march build work; in the end, the papra-pcb issue of not having the proper cable for the dust-proof connector needs to be solved.

**Comment by mmroden** [comment]
Closing as not to be done; ended up doing connectors as spec'd.  The STL exists and we built it, but it's not a good idea.

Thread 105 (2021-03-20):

tetrabiodistributed/papr-print-files #105: add louvers to the filter cover

mmroden, 2021-03-20:
must determine the direction before designing can start, likely a conversation about how to mount the devices.

Judoguy12, 2021-04-09:
I  have tested this, for light rain the louvres are too small to prevent water hitting the filter, they need to be much larger to be effective. They printed nicely though

darraghbr, 2021-04-09:
There are a couple of ways that you can take this, you can either go mushroom cowl style, where you have a curved section that stands off from the body of the PAPRA and allows air to come in through a circuitous path. Something similar to below. I would suggest that the 'open' area is nominally similar to the intake area of the fan we are using. If you wanted to you could make the cowl draw in air only from the bottom and sides of the PAPRA, leaving the top completely closed. 

[image]

The other way you can do this is more conventional louvers. A profile like shown below is pretty common. You could use some solid sections at points across the 'span' to aid in printing and in ridigity of the final component. 

[image]

closed 2021-05-13 by mmroden

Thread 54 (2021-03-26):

### ISSUE TITLE
Document how fan boxes are tested

### ISSUE THREAD

**Issue by mmroden** [tetrabiodistributed/papr-print-files#54]
with the portacount?

**Comment by mmroden** [comment]
repurposing sampling devices for this purpose
scoring in the range between N95 and N99
Daniel can help

**Comment by DHHwangPhD** [comment]
![image](https://user-images.githubusercontent.com/68876187/108606511-47e9c980-736f-11eb-8b40-167a1f3e8335.png)
We test by connecting the TSI PortaCount 8048 to the mask. We also test the box itself with the PortaCount.

**Comment by mmroden** [comment]
Can be solved with a video showing the portacount setup with the box.  Ideally showing both the box and mask testing setups, and would require test results for various boxes.

**Comment by mmroden** [comment]
Documented in the march docs

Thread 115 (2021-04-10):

tetrabiodistributed/papr-print-files #115: Black wall on M12 controller at 2 layers blocks LED

mechatroniks-git, 2021-04-10:
Current limiting resistor for LED swapped out to 100 ohms, LED is driven at 18mA

[image]

mmroden, 2021-04-12:
Not a problem for the pink papr

mmroden, 2021-04-12:
not a problem for grey-- blue may not shine through black very well?  Maybe spec a brighter LED?

mmroden, 2021-04-12:
we do need to spec the specific LED.  Don't have a problem with superbrights, because have to go through plastic.  Didn't matter with direct exposure with the light pipe, but now that the light pipe is encased in plastic, should use superbrights

mmroden, 2021-04-12:
targeting a red LED

mmroden, 2021-04-12:
red LEDs are hard to get right now, may have to look at a different color.

mechatroniks-git, 2021-04-12:
Blue LED: https://www.we-online.de/katalog/datasheet/150080BS75000.pdf
With 100ohm LEDs, we were driving the led at about 18mA, which is about 135mcd. These LEDs have a 140° viewing angle, which is close to the 160° recommended [here](https://vcclite.com/light-pipe-faqs/#:~:text=For%20ideal%20illumination%20whether%20using,viewing%20angle%20of%20160%20degrees.). 

[image]

mechatroniks-git, 2021-04-12:
Recommend using this [JLC LED](https://lcsc.com/product-detail/Light-Emitting-Diodes-LED_Foshan-NationStar-Optoelectronics-NCD0603G1_C84267.html) see [datasheet](https://datasheet.lcsc.com/szlcsc/2008201032_Foshan-NationStar-Optoelectronics-NCD0603G1_C84267.pdf)

mechatroniks-git, 2021-04-24:
[image]

mmroden, 2021-05-13:
Don't print it in black; make sure to document

closed 2021-07-17 by mmroden

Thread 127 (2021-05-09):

tetrabiodistributed/papr-print-files #127: PETG prints still not perfect

mechatroniks-git, 2021-05-09:
Seeing issues on the longer parts:
Ender 3 Pro  with blobs/boogers
Prusa has ripples on the inside
Makerbot M12 controllers were fine

argus1, 2021-05-13:
trying transparent PETG

mechatroniks-git, 2021-05-16:
I printed a temperature tower, found that 235'C worked well for MH Build PETG on Replicator 2
Simplify3D settings:
- Bed temp at 80'C (layer 1) then 55'C (layer 2+)
- Extrusion multiplier .99
- Extrusion width .45mm (Nozzle dia .4mm)
- Retraction set to 4mm
- Retraction speed 1800mm/min
- .3mm Coasting distance
- 1.0mm Wipe Distance
- Downward cooling fan set to 40%
- Print speed 3500 mm/min

mmroden, 2021-08-14:
@capsulecorplab can test on his ender3, he has new cura profiles

capsulecorplab, 2021-08-14:
@mechatroniks-git which parts in particular were having issues?

mechatroniks-git, 2021-08-14:
M12 controller was having print quality issues from the non-makerbot machines, as noted during build party.

capsulecorplab, 2021-08-14:
I'm currently printing at 250 with fan speed at 100%

mmroden, 2021-08-18:
Need to define what printed parts are acceptable and how we determine that acceptability

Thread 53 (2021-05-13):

### ISSUE TITLE
CPAP hose falls off of fan box fairly easily

### ISSUE THREAD

**Issue by mmroden** [tetrabiodistributed/papr-print-files#53]
The hose fell off twice when wearing the PAPR to a park for three hours, which should not happen.

**Comment by darraghbr** [comment]
Perhaps a solution for the hoses coming off?

https://racesparesuk.com/product/brembo-reservoir-pipe-clip/

Could use a circlip and groove style of retention?

**Comment by mmroden** [comment]
Also test heat shrink on the tubing

**Comment by mmroden** [comment]
Will be solved by #14.  Silicone cuff seals are intended to be added/removed multiple times.

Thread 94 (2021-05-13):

### ISSUE TITLE
How to waterproof/splashproof the papra?

### ISSUE THREAD

**Issue by mmroden** [tetrabiodistributed/papr-print-files#94]

**Comment by mechatroniks-git** [comment]
To make water-resistant, we would need to add seals to the housing, use the IP68 rated DC jack on the M12 PCB and add conformal coating on the PCBA. https://www.mgchemicals.com/products/conformal-coating/silicone-conformal-coatings/silicone-modified-conformal-coating/

**Comment by mmroden** [comment]
Goal is splashproof/Englandproof.  Not for direct rainshowers, but for mist/running use cases.  Will be closed by #102, #103, #105

**Comment by mmroden** [comment]
closed by #113, but needs to be tested

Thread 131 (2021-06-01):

### ISSUE TITLE
Fan Box Assembly Diagram

### ISSUE THREAD

**Issue by mmroden** [tetrabiodistributed/papr-print-files#131]
Need a fan box assembly diagram for the documentation

**Comment by argus1** [comment]
seems to be misalignment of the screw holes for the fanbox and the base plate, is user-rescale is required?

**Comment by mmroden** [comment]
Which misalignment are you seeing?  Maybe a picture to show the problem?

**Comment by argus1** [comment]
nevermind, I think my printer shrunk the baseplate, I would scale down the box, but likely the fan won't fit after that.

**Comment by mmroden** [comment]
closed by #147

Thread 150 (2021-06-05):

tetrabiodistributed/papr-print-files #150: Check a fan taper to see if it will work with this model fan

mmroden, 2021-06-05:
Design the taper for testing to see if we can get to the 4 CFM requirement

https://www.digikey.co.uk/product-detail/en/sunon-fans/PF97331B1-B00U-A99/259-1925-ND/6189086

or

https://www.cuidevices.com/product/thermal-management/dc-fans/centrifugal-blowers/cbm-97b-series

mechatroniks-git, 2021-06-07:
Snapshot of distributor stock:

[image]

[image]

darraghbr, 2021-06-07:
https://www.digikey.co.uk/product-detail/en/delta-electronics/BFB1012EH-A/603-2105-ND/9351771

mechatroniks-git, 2021-06-07:
[image]

mechatroniks-git, 2021-06-21:
Results from testing. Blower inlet to open air, short cone "TestFunnelShort" taped to blower with 36 inches of blue hose to Sensirion to open air. 

[image]

All 3 blowers would require a 11V minimum to meet 4CFM. The M12 battery will start at 12.4V and drain down to 8.4V, making the CUI CBM-120B series a better fit with our battery and electronics. See [prior test](https://github.com/tetrabiodistributed/papr-print-files/issues/151#issuecomment-856045012)

mmroden, 2021-07-07:
This work is done, we know we need to hit 4CFM

closed 2021-07-07 by mmroden

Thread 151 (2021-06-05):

tetrabiodistributed/papr-print-files #151: Test the fan taper to ensure that 4 CFM is hit

mmroden, 2021-06-05:
blocked on #150 ; once we have a fan taper, we can then redesign the box for the fan

mechatroniks-git, 2021-06-07:
**Airflow tests with OLD funnel**

NMB BG1203-B045-00S FAN + FUNNEL + 36" BLUE HOSE + FLOW SENSOR
12V | .44A | 52SLM

**Airflow tests with NEW funnel**

NMB BG1203-B045-00S FAN + FUNNEL + 36" BLUE HOSE + FLOW SENSOR
12V | .51A | 70SLM

UTUO FAN + FUNNEL + 36" BLUE HOSE + FLOW SENSOR
12V | .33A | 60SLM

We see improvement, but not enough to hit the target

mechatroniks-git, 2021-06-07:
Tested the CUI blower without disassembling (in fan box with HEPA filter) using the legacy funnel as attached. 

We able to get 4CFM easily at around 8V & 2A.  Could be a drop in solution to our challenges. The voltage range matches up with the M12 battery and controller electronics. 

[image]

mmroden, 2021-07-07:
This is done in the sense that we know the answer; the taper has been defined and models must be made

closed 2021-07-07 by mmroden

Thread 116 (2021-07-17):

### ISSUE TITLE
BNC on PCB nuts require 9/16" nut driver, 14mm was used successfully

### ISSUE THREAD

**Issue by mechatroniks-git** [tetrabiodistributed/papr-print-files#116]

**Comment by mmroden** [comment]
Will have to spec this out, there are two different sizes-- box is 5/8, controller is 15mm, so maybe have to get more compatible parts?

**Comment by mmroden** [comment]
have to order a separate nut for what goes on the board, not sure if we can find one that fits that threading.

**Comment by mmroden** [comment]
Documentation issue to make sure we capture the proper nut drivers.  Need a deep socket set or an adjustable wrench

**Comment by mmroden** [comment]
Moved to docs repo

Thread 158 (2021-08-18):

tetrabiodistributed/papr-print-files #158: Investigate new BNC cables

mmroden, 2021-08-18:
Need to update the BNC cables in the BOM to reflect the proper gauge for the power draw

mechatroniks-git, 2021-08-18:
Options:
20 awg - https://www.jameco.com/z/205-523-Steren-Electronics-Cable-Assembly-RG58-U-36-Bnc-To-Bnc-50-Ohm_11404.html

26 awg (rated for 2.2A)- https://www.jameco.com/z/G7402-R-Jameco-Valuepro-Cable-Assembly-Rg174-U-3-BNC-to-BNC-50-Ohm_111473.html

mmroden, 2021-08-23:
Kevin to help review

mmroden, 2021-08-28:
"V-MCM-6641T11	" will be tested

mmroden, 2021-09-13:
New BNC cable worked.

mmroden, 2021-09-13:
Apparently "plug it in and it works" isn't enough.  My bad.

mechatroniks-git, 2021-09-20:
@DHHwangPhD Which BNC did you order from McMaster?
Either one of these would work
[image]

From [Engineering Toolbox](https://www.engineeringtoolbox.com/wire-gauges-d_419.html), we're good to 5A

[image]

mmroden, 2021-11-04:
max amperage we have in current models is 1.3-1.4, so maybe target 2 amps so we have a lot of breathing room.

22 gauge should be more than fine, 24 gauge should also be OK if we can find it.

RG-59/U will work.

closed 2021-11-04 by mmroden

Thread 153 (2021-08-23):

### ISSUE TITLE
SPIKE: explore AAF filter material

### ISSUE THREAD

**Issue by mmroden** [tetrabiodistributed/papr-print-files#153]
Check to see if AAF has a filter that we can use:
https://www.aafintl.com/en/commercial/browse-products/commercial/hepa-ulpa-filters

**Comment by argus1** [comment]
using the following DIMENSIONS 6.29 x 3.97 x 0.78 in

**Comment by argus1** [comment]
AAF relays that MegaCel II ePTFE has a thickness of 50mm for optimal filtration

**Comment by argus1** [comment]
following up to see if further adaptation is possible

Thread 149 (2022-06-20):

### ISSUE TITLE
People complain that masks hit them on the chin

### ISSUE THREAD

**Issue by mmroden** [tetrabiodistributed/papr-print-files#149]
People are complaining that the masks hit them on the chin; they expect the mask to go under the chin, like a cloth mask.  Just something to think about viz designs.

**Comment by MarkPorter66** [comment]
is this a real issue?

**Comment by mmroden** [comment]
Well, they don't want to wear the masks, so...

**Comment by mmroden** [comment]
Closing because we know we need better/different masks

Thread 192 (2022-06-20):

### ISSUE TITLE
3M respirator adapter not properly mounting

### ISSUE THREAD

**Issue by capsulecorplab** [tetrabiodistributed/papr-print-files#192]
The 3M respirator adapter has issues clipping and staying onto [3M half facepiece reusable respirator mask](https://www.amazon.com/3M-Respirator-6300-Respiratory-Protection/dp/B007JZ1MK6/)
![2021-10-24 17 18 41](https://user-images.githubusercontent.com/14095576/154133057-40bc77a1-0fdd-4901-9d49-3dbe8b9a735b.jpg)
![2021-10-24 17 19 20](https://user-images.githubusercontent.com/14095576/154133065-b7760f09-768a-410a-9b68-a2c487ac5e67.jpg)
![2021-10-24 17 20 38](https://user-images.githubusercontent.com/14095576/154133075-2eb59c56-7197-4cf0-8636-2b45eb30bd14.jpg)

**Comment by mmroden** [comment]
Closed by #212, the attachment points come through the side with no source control (yet!)

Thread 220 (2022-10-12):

tetrabiodistributed/papr-print-files #220: The pressure tap model needs to get built

mmroden, 2022-10-12:
I've got a pull request set up for the pressure tap setup, but unfortunately, Prusa Slicer won't remove negative spaces.  So, I need someone to remove the negative spaces as per the attached image (ie, only about a mm thickess)

[image]

mmroden, 2022-10-15:
[Pressure Tap v3.zip](https://github.com/tetrabiodistributed/papr-print-files/files/9792716/Pressure.Tap.v3.zip)
Here is the 3mf file that is the source

Judoguy12, 2022-11-02:
I have no thin walls on my slicer although it appears to be very thin walls so would be better suited to resin

mmroden, 2022-11-02:
@DHHwangPhD has an updated model for this, would need a PR to close using that model with a new part number.  I may just do that right now

mmroden, 2022-11-03:
Closed by #224

closed 2022-11-03 by mmroden

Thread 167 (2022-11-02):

### ISSUE TITLE
eFuse tripping when run at lower amperage

### ISSUE THREAD

**Issue by mechatroniks-git** [tetrabiodistributed/papr-print-files#167]
When the fan box is run at less than full amperage (not 2.8, but around 2.2), the efuse trips.  At this amperage, the fan box will cycle between being on and off.

**Comment by mmroden** [comment]
Parts are ordered, gonna build those out.

**Comment by mechatroniks-git** [comment]
Testing/evaluation
1. Test trip current 
2. Test undervoltage 
3. Test overvoltage
4. Test reverse polarity
5. Test fuse thru full PWM range at PWM freq, using highest current draw blower

**Comment by mmroden** [comment]
Resolved by the current papra-pcb.

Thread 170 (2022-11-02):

### ISSUE TITLE
Investigate 30mm hosing to determine if that will relieve the battery life pressure

### ISSUE THREAD

**Issue by mmroden** [tetrabiodistributed/papr-print-files#170]
30mm hoses that split to 2 22mm hoses may work well for more flow coming out of the system

**Comment by darraghbr** [comment]
I've done some quick calculations and I think we would see between 2 and 5% flow rate increase moving from a 22mm to a 30mm hose, depending on the fan

[30mm hose airflow.pdf](https://github.com/tetrabiodistributed/papr-print-files/files/7209636/30mm.hose.airflow.pdf)
.

**Comment by mmroden** [comment]
Here is the hosing to buy: https://www.mcmaster.com/hose/id~30mm/

**Comment by mmroden** [comment]
3d crowd did this testing, Mark Porter will need to provide

**Comment by mmroden** [comment]
This did not seem to work.

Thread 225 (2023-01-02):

tetrabiodistributed/papr-print-files #225: approach for keeping git commits and Fusion360 design history in sync

capsulecorplab, 2023-01-02:
as follow up to https://github.com/tetrabiodistributed/papra/issues/99, Fusion users need a means to reference git commits in Fusion360 design history.

Desired outcomes:
- export process for Fusion model bodies as STEP/STL
- process for creating a git commit directly from Fusion design history save point (including version description notes for commit message)
- process for re-configuring python environment to not break per Fusion updates

Burhan-Q, 2023-01-07:
# References:

## Fusion360 Python
[Fusion360 GitHub](https://github.com/AutodeskFusion360)
[OctoFusion](https://github.com/tapnair/OctoFusion) good reference for Add-In for Fusion, look to use for following our documented approach for file naming assistance
[tapnair F360 repos](https://github.com/tapnair)
[tapnair personal page](https://tapnair.github.io/index.html#general_anchor) Also good for reference to UI elements

## python module imports for F360
[method1](https://forums.autodesk.com/t5/fusion-360-api-and-scripts/import-data-from-excel-type-xlsx/m-p/11245348/highlight/true#M16701)
[method2](https://forums.autodesk.com/t5/fusion-360-api-and-scripts/importing-modules-error-importerror-no-module-named-openpyxl/td-p/8512051)

## python control for GitHub 
https://github.com/PyGithub/PyGithub
- request records of commits? [get_commits](https://pygithub.readthedocs.io/en/latest/github_objects/Repository.html#github.Repository.Repository.get_commits) 
- create new commit? [create_git_commit](https://pygithub.readthedocs.io/en/latest/github_objects/Repository.html#github.Repository.Repository.create_git_commit)
- blob, not sure if we need it, but blob [create_git_blob](https://pygithub.readthedocs.io/en/latest/github_objects/Repository.html#github.Repository.Repository.create_git_blob)
- maybe could use to generate text/csv file with the parts exported with the FusionVersionID numbers in case files are not uploaded [create_file](https://pygithub.readthedocs.io/en/latest/github_objects/Repository.html#github.Repository.Repository.create_file)

Burhan-Q, 2023-01-07:
@capsulecorplab will look into figuring out the GitHub controls

Burhan-Q, 2023-01-07:
[FusionDataUtils](https://github.com/tapnair/FusionDataUtils) could be helpful if looking to capture additional from Fusion

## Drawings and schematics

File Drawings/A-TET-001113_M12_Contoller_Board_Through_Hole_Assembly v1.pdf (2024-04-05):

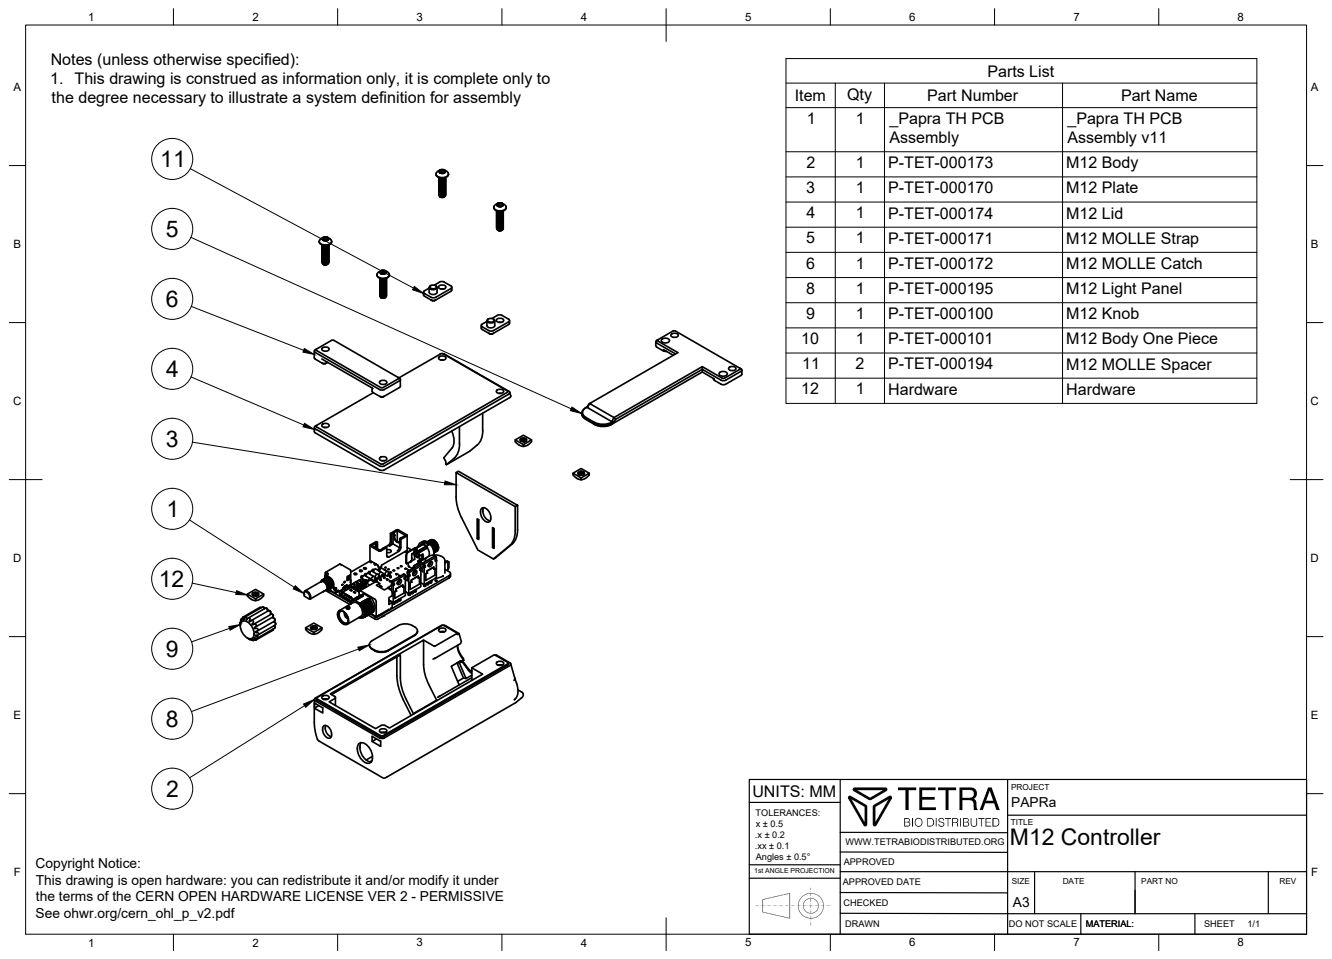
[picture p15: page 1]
UNITS: MM; Angles ± 0.5° 1st ANGLE PROJECTION; SIZE; DATE; PART NO; DO NOT SCALE; MATERIAL:; APPROVED DATE; M12 Controller; Parts List

Notes (unless otherwise specified):
1. This drawing is construed as information only, it is complete only to
the degree necessary to illustrate a system definition for assembly

Item | Qty | Part Number | Part Name
1 | 1 | _Papra TH PCB Assembly | _Papra TH PCB Assembly v11

2 | 1 | P-TET-000173 | M12 Body
3 | 1 | P-TET-000170 | M12 Plate
4 | 1 | P-TET-000174 | M12 Lid
5 | 1 | P-TET-000171 | M12 MOLLE Strap
6 | 1 | P-TET-000172 | M12 MOLLE Catch
8 | 1 | P-TET-000195 | M12 Light Panel
9 | 1 | P-TET-000100 | M12 Knob
10 | 1 | P-TET-000101 | M12 Body One Piece
11 | 2 | P-TET-000194 | M12 MOLLE Spacer
12 | 1 | Hardware | Hardware

WWW.TETRABIODISTRIBUTED.ORG

Copyright Notice:
This drawing is open hardware: you can redistribute it and/or modify it under
the terms of the CERN OPEN HARDWARE LICENSE VER 2 - PERMISSIVE
See ohwr.org/cern_ohl_p_v2.pdf

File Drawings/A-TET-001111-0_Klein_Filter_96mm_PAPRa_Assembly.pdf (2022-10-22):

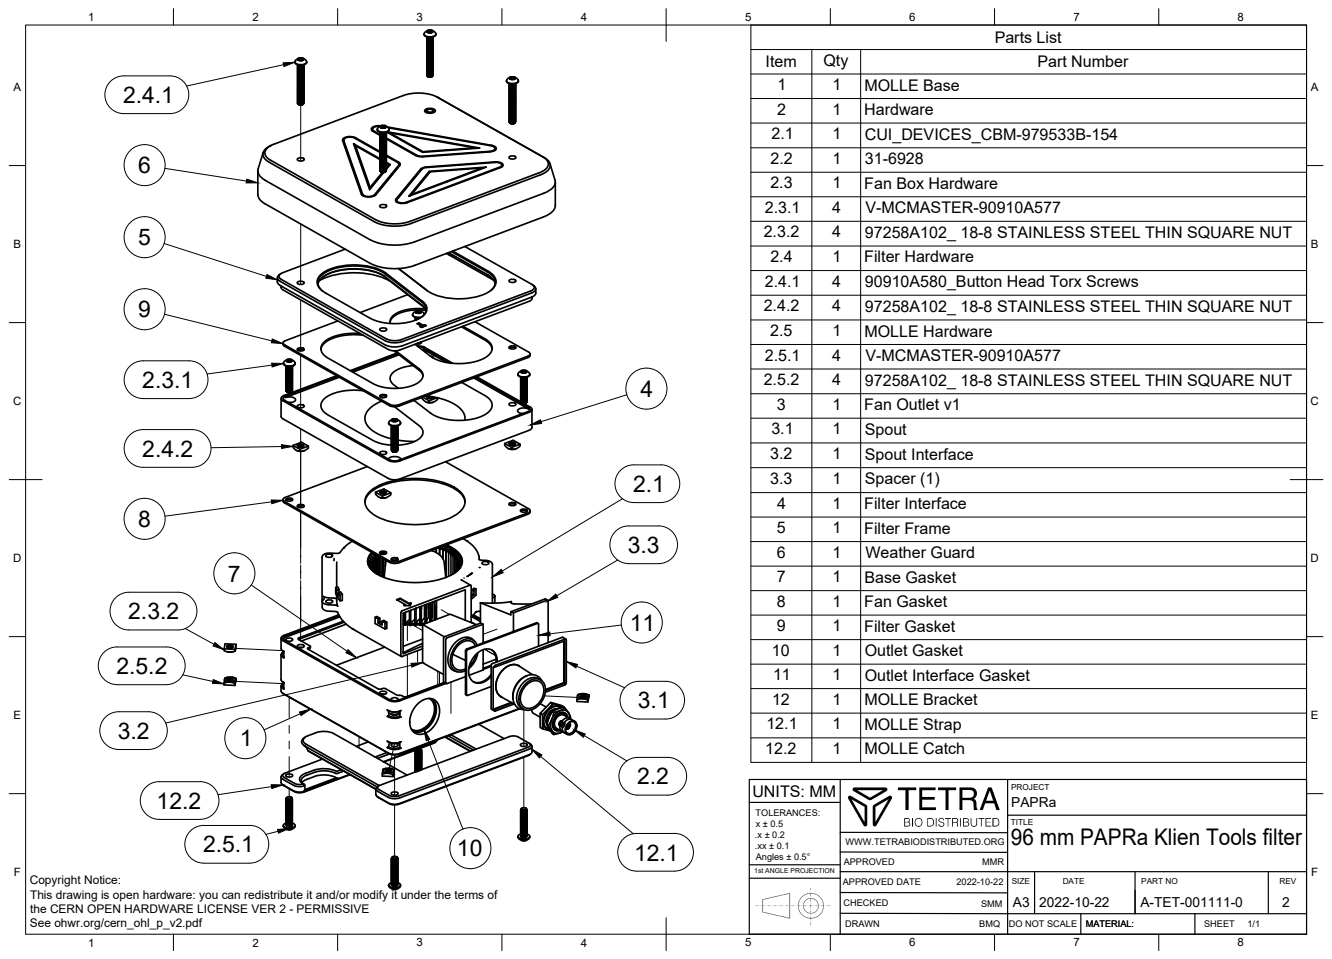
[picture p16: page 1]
UNITS: MM; Angles ± 0.5° 1st ANGLE PROJECTION; SIZE; DATE; PART NO; DO NOT SCALE; MATERIAL:; APPROVED DATE; Parts List; MOLLE Catch 1

Item | Qty | Part Number
1 | 1 | MOLLE Base
2 | 1 | Hardware
2.1 | 1 | CUI_DEVICES_CBM-979533B-154
2.2 | 1 | 31-6928
2.3 | 1 | Fan Box Hardware
2.3.1 | 4 | V-MCMASTER-90910A577
2.3.2 | 4 | 97258A102_ 18-8 STAINLESS STEEL THIN SQUARE NUT
2.4 | 1 | Filter Hardware
2.4.1 | 4 | 90910A580_Button Head Torx Screws
2.4.2 | 4 | 97258A102_ 18-8 STAINLESS STEEL THIN SQUARE NUT
2.5 | 1 | MOLLE Hardware
2.5.1 | 4 | V-MCMASTER-90910A577
2.5.2 | 4 | 97258A102_ 18-8 STAINLESS STEEL THIN SQUARE NUT
3 | 1 | Fan Outlet v1
3.1 | 1 | Spout
3.2 | 1 | Spout Interface
3.3 | 1 | Spacer (1)
4 | 1 | Filter Interface
5 | 1 | Filter Frame
6 | 1 | Weather Guard
7 | 1 | Base Gasket
8 | 1 | Fan Gasket
9 | 1 | Filter Gasket
10 | 1 | Outlet Gasket
11 | 1 | Outlet Interface Gasket
12 | 1 | MOLLE Bracket
12.1 | 1 | MOLLE Strap

PROJECT
PAPRa
96 mm PAPRa Klien Tools filter

WWW.TETRABIODISTRIBUTED.ORG

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

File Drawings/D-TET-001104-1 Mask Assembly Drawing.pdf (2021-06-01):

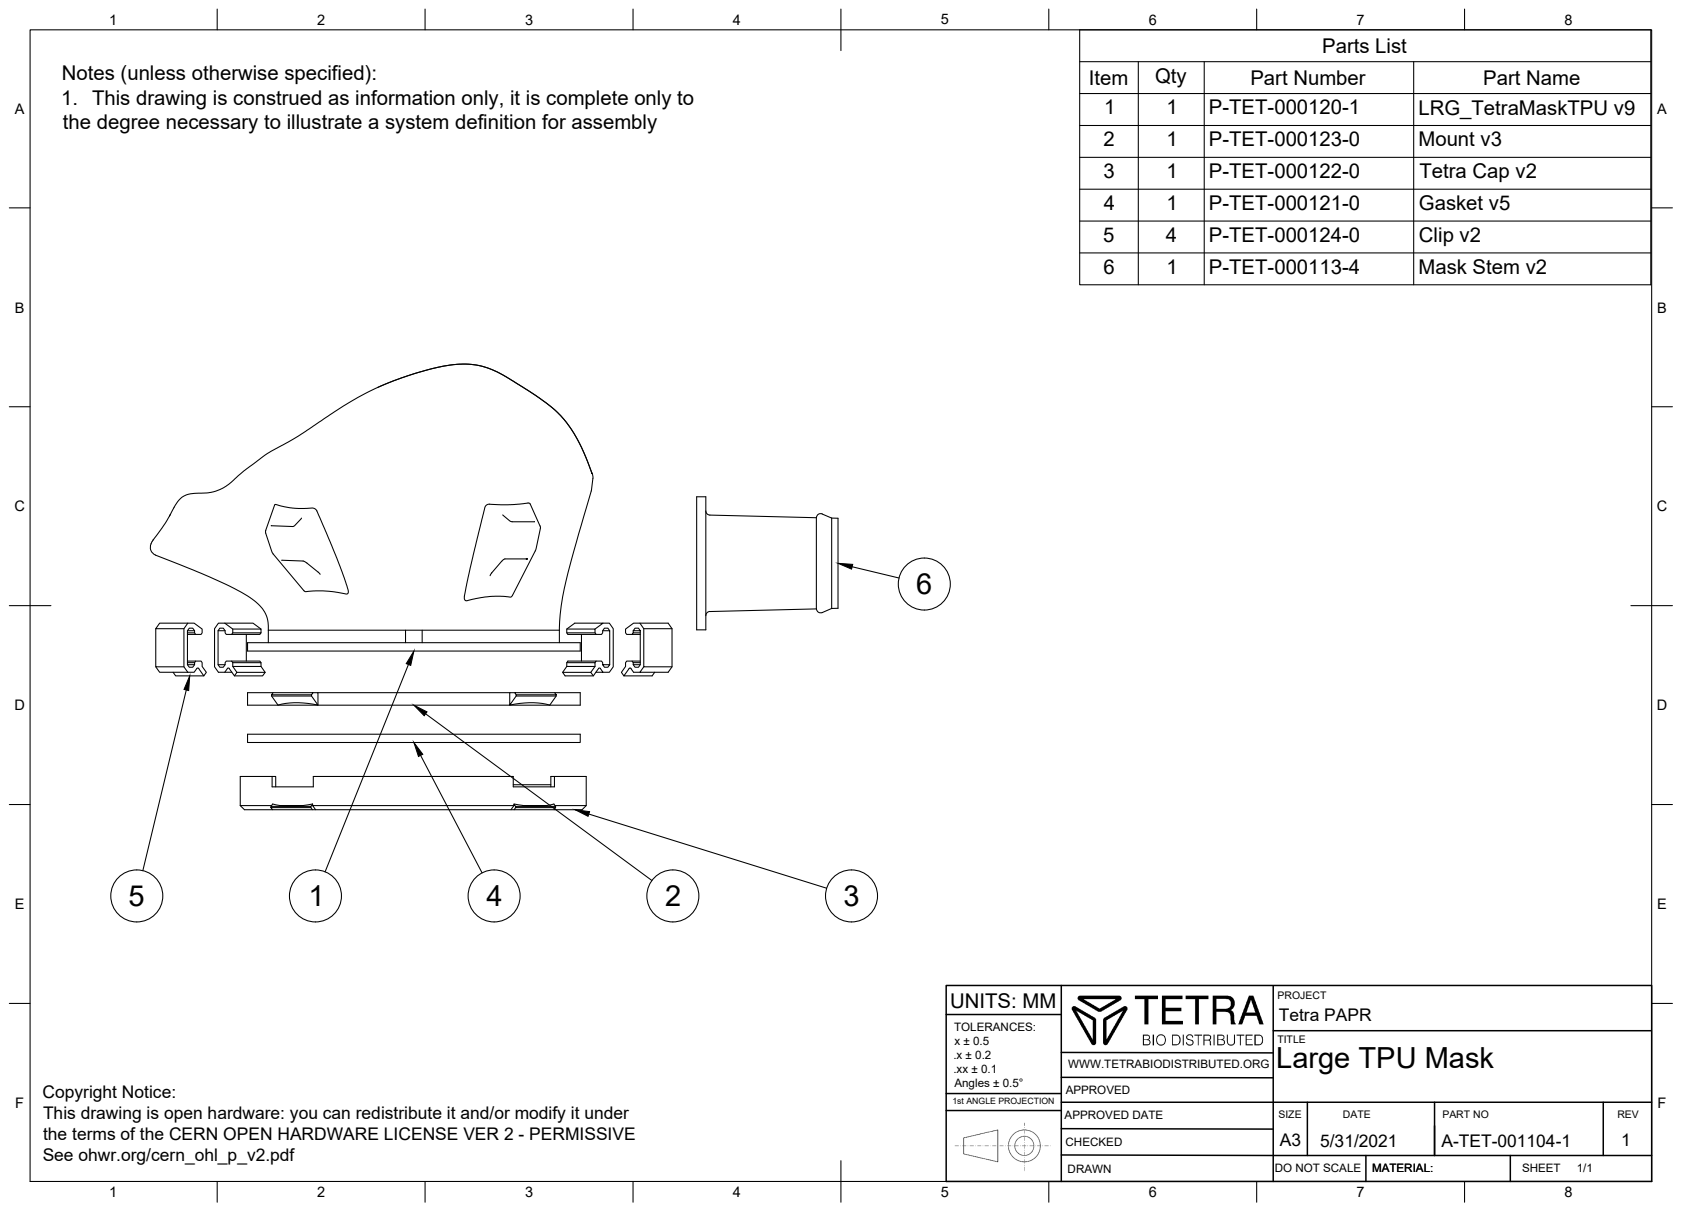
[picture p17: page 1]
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

Item | Qty | Part Number | Part Name
1 | 1 | P-TET-000120-1 | LRG_TetraMaskTPU v9
2 | 1 | P-TET-000123-0 | Mount v3
3 | 1 | P-TET-000122-0 | Tetra Cap v2
4 | 1 | P-TET-000121-0 | Gasket v5
5 | 4 | P-TET-000124-0 | Clip v2
6 | 1 | P-TET-000113-4 | Mask Stem v2

PROJECT
Tetra PAPR
Large TPU Mask

WWW.TETRABIODISTRIBUTED.ORG

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

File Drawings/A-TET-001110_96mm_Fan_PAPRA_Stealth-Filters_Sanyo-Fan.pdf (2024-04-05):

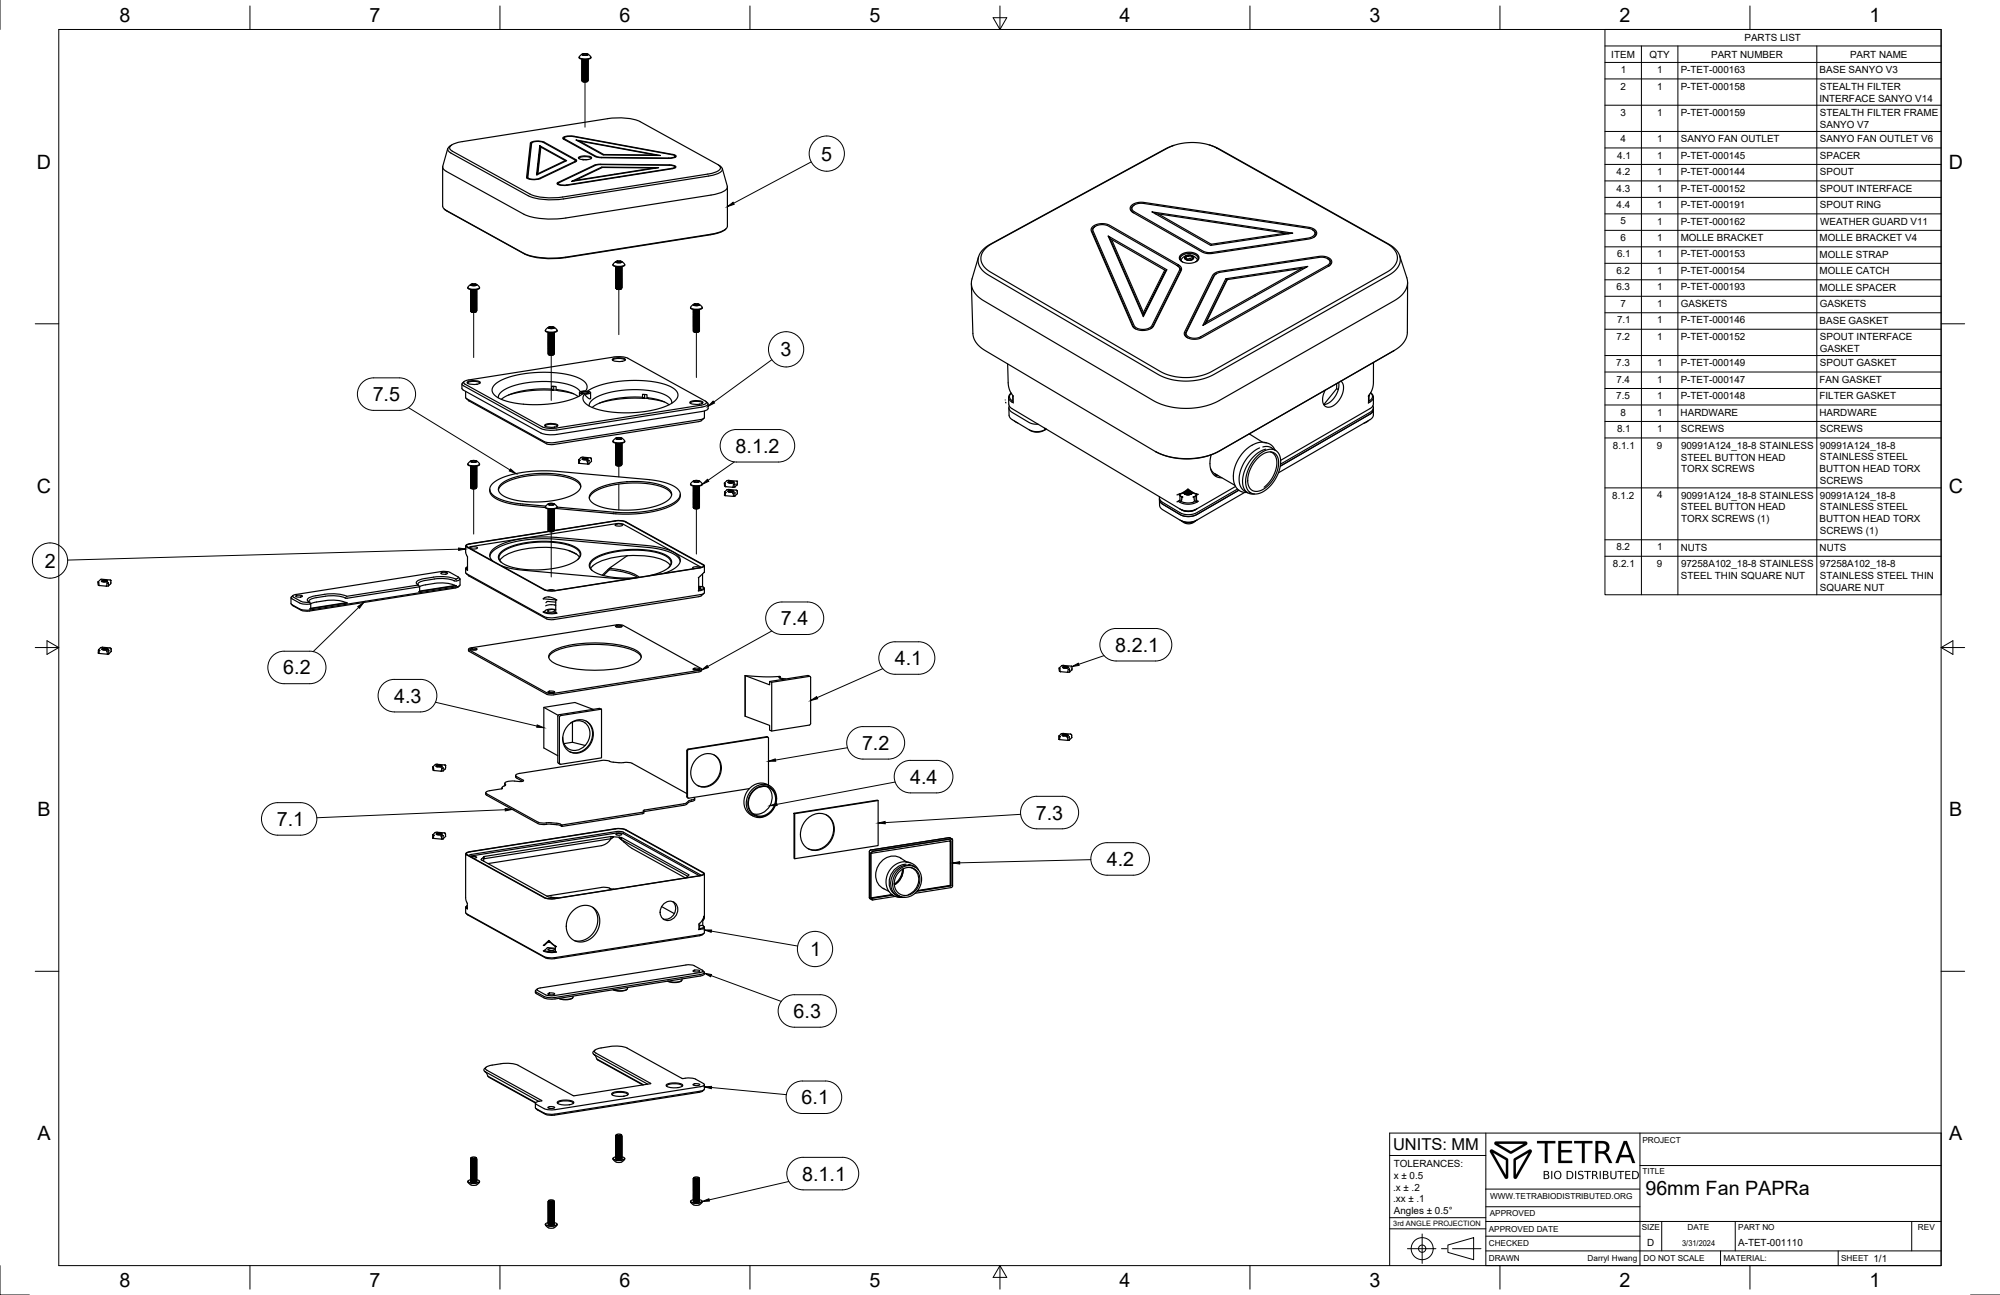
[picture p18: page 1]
BCD ABCD; APPROVED DATE; DO NOT SCALE; MATERIAL:; SHEET; SIZE; DATE; PART NO; REV; UNITS: MM; x ± 0.5 .x ± .2 .xx ± .1 Angles ± 0.5°; 3rd ANGLE PROJECTION; Darryl Hwang; A-TET-001110; 96mm Fan PAPRa; PARTS LIST; P-TET-000191; SPOUT RING 5; P-TET-000162; WEATHER GUARD V11 6; MOLLE BRACKET; MOLLE BRACKET V4

ITEM | QTY 1 1 | P-TET-000163 P-TET-000158 PART NUMBER | BASE SANYO V3 2 STEALTH FILTER PART NAME 1

1 | P-TET-000159 | INTERFACE SANYO V14 3 STEALTH FILTER FRAME

1 | SANYO FAN OUTLET | SANYO V7 4 SANYO FAN OUTLET V6

4.1 | 1 | P-TET-000145 | SPACER
4.2 | 1 | P-TET-000144 | SPOUT
4.3 | 1 | P-TET-000152 | SPOUT INTERFACE

6.1 | 1 | P-TET-000153 | MOLLE STRAP
6.2 | 1 | P-TET-000154 | MOLLE CATCH
6.3 | 1 1 | P-TET-000193 GASKETS | MOLLE SPACER 7 GASKETS

7.1 | 1 | P-TET-000146 | BASE GASKET
7.2 | 1 | P-TET-000152 | SPOUT INTERFACE GASKET

7.3 | 1 | P-TET-000149 | SPOUT GASKET
7.4 | 1 | P-TET-000147 | FAN GASKET
7.5 | 1 1 | HARDWARE P-TET-000148 | FILTER GASKET 8 HARDWARE

8.1 | 1 | SCREWS | SCREWS
8.1.1 | 9 | 90991A124_18-8 STAINLESS STEEL BUTTON HEAD TORX SCREWS | 90991A124_18-8 STAINLESS STEEL BUTTON HEAD TORX SCREWS

8.1.2 | 4 | 90991A124_18-8 STAINLESS STEEL BUTTON HEAD TORX SCREWS (1) | 90991A124_18-8 STAINLESS STEEL BUTTON HEAD TORX SCREWS (1)

8.2 | 1 | NUTS | NUTS
8.2.1 | 9 | 97258A102_18-8 STAINLESS STEEL THIN SQUARE NUT | 97258A102_18-8 STAINLESS STEEL THIN SQUARE NUT

WWW.TETRABIODISTRIBUTED.ORG

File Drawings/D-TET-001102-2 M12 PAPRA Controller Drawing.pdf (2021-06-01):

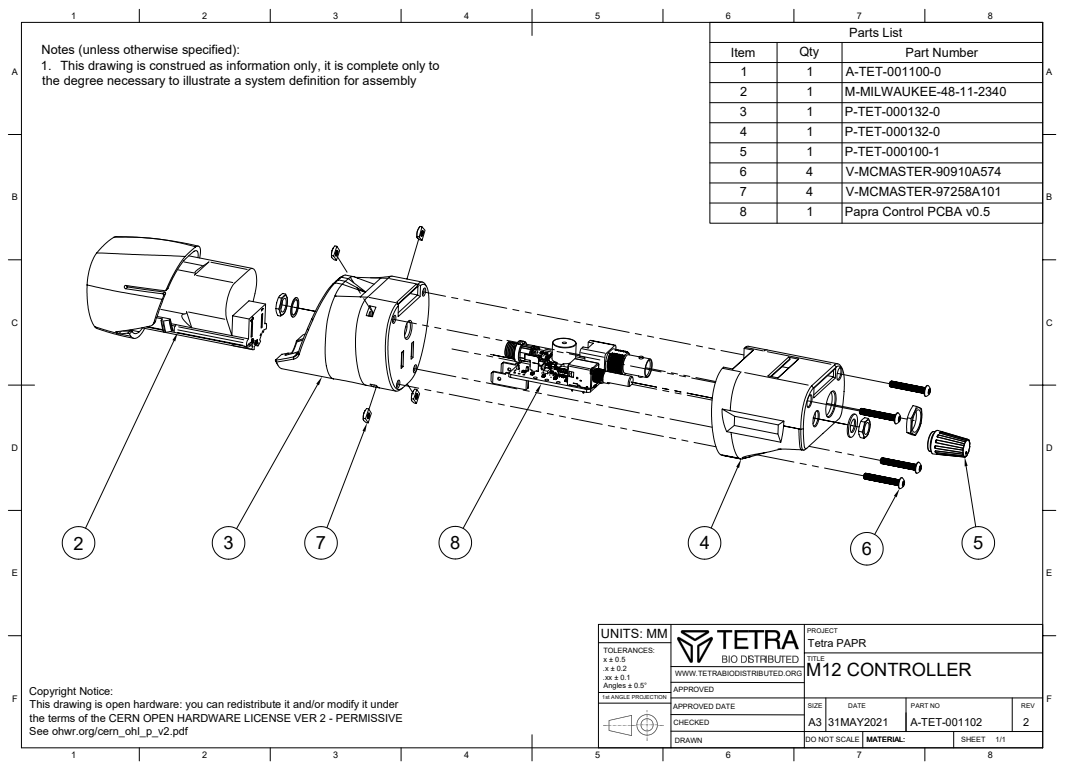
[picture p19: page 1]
8 BCDEF; ABCDEF PROJECT TITLE; REV UNITS: MM TOLERANCES: x ± 0.5 .x ± 0.2 .xx ± 0.1 Angles ± 0.5° 1st ANGLE PROJECTION; SIZE; DATE; PART NO DO NOT SCALE; MATERIAL: A3 DRAWN; MATERIAL: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

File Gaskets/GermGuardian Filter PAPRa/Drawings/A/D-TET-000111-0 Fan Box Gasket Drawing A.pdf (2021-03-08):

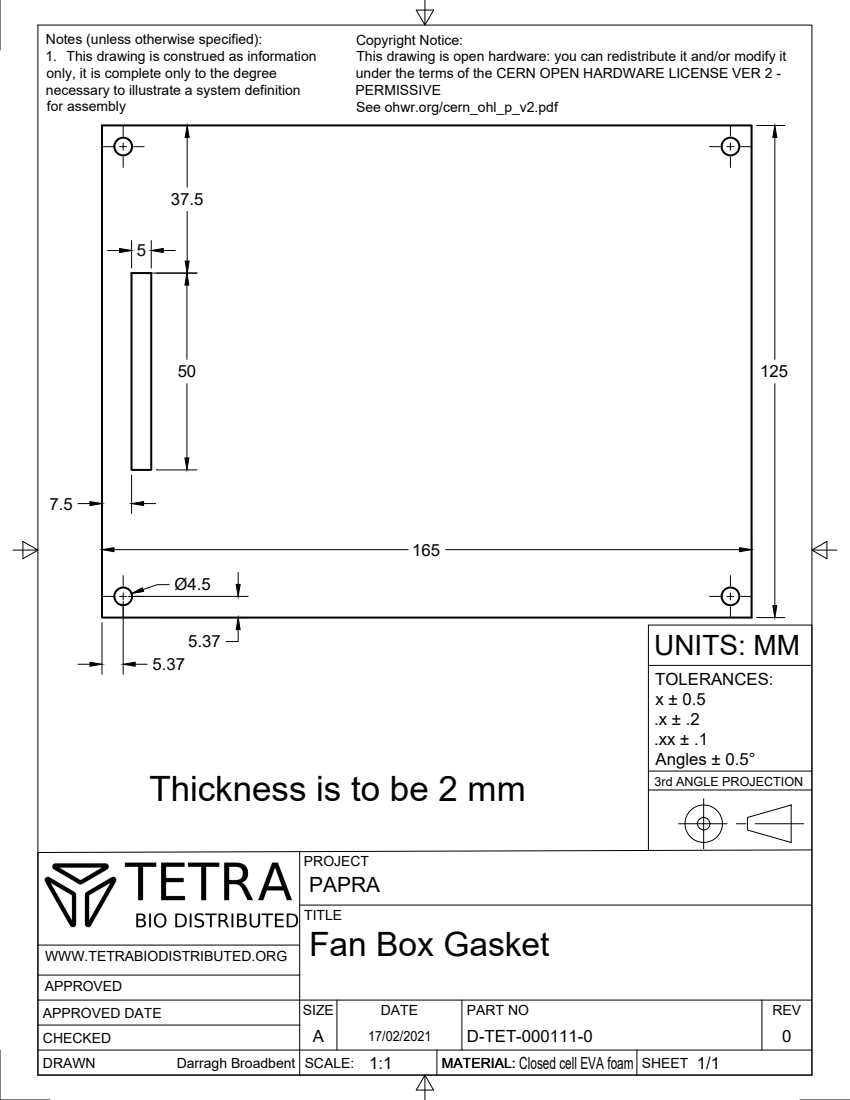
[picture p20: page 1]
APPROVED DATE; SIZE; DATE; PART NO; REV; UNITS: MM; x ± 0.5 .x ± .2 .xx ± .1 Angles ± 0.5°; 3rd ANGLE PROJECTION; SCALE:; MATERIAL: Closed cell EVA foam; Darragh Broadbent

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

Thickness is to be 2 mm

PROJECT
PAPRA
Fan Box Gasket

WWW.TETRABIODISTRIBUTED.ORG

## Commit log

2020-10-22 committing the STL files used to build on October 19, 2020
    [Cover.stl, DoubleFunnelThin.stl, FanBox.stl, LargeMaskDoublePC.stl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]
2020-10-24 adding in gaskets
    [BoxGasket.stl, FilterGasket.stl]
2021-01-11 removing old stls, adding new ones
    [Base Plate.stl, BoxGasket.stl, Cover.stl, DoubleFunnelThin.stl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]
2021-01-19 adding in new STLs and gaskets
    [FitMaskClip.stl, FitMaskHoneycombCap.stl, FitMaskMount.stl, LRG_facefitter_V1-6-1-Inner-Ring.STL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]
2021-01-23 Adding Knob STL
    [M12 Controller Knob.stl]
2021-01-28 cleaning up STLs for Jan 30th Build
    [Base Plate.stl, Fan Box.stl, FitMaskClip.stl, FitMaskHoneycombCap.stl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]
2021-01-28 Current design and part numbers added
    [M12 Controller Body.stl, M12 Controller Knob.stl, M12 Controller Lid.stl, M12 Controller Plate.stl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]
2021-01-28 updating part rev
    [P-TET-000103-0 M12 Controller Plate.stl]
2021-01-29 Part numbers and tweaks for fan box
    [Base Plate.stl, Fan Box.stl, P-TET-000104-0 M12 Light Pipe Clip.stl, P-TET-000110-0 Fan Box Base Plate.stl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]
2021-01-29 Knob re-export
    [P-TET-000100-0 M12 Controller Knob.stl]
2021-01-29 Fixed manifold error on P-TET-000101-0
    [P-TET-000101-0 M12 Controller Body.stl]
2021-01-29 Fixed P-TET-000116-0 as it behaved wierdly in slicer
    [P-TET-000116-0 Fan Box UniFrameCover.stl]
2021-02-03 Updating M12 Controller Plate to -1
    [P-TET-000103-1 M12 Controller Plate.stl]
2021-02-06 Scaled part by 2% for fit from V-0
    [P-TET-000100-1 M12 Controller Knob.stl]
2021-02-06 Delete P-TET-000100-0 M12 Controller Knob.stl
    Older version too small
    [P-TET-000100-0 M12 Controller Knob.stl]
2021-02-06 Contours for S/M/L NIOSH headforms
    Closes issues #47, #46, and #45
    [LRG_face_surface-full.STEP, LRG_face_surface-full_5mm.STEP, LRG_face_surface.DXF, LRG_face_surface.STEP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]
2021-02-10 Updates to Controller Plate
    [P-TET-000103-0 M12 Controller Plate.stl, P-TET-000103-1 M12 Controller Plate.stl]
2021-02-13 removing the orphan battery controller plate not in the right directory
    [P-TET-000103-1 M12 Controller Plate.stl]
2021-02-13 Create PAPR_facefit_strap_tie-points.STEP
    Closes #50
    [PAPR_facefit_strap_tie-points.STEP]
2021-02-13 Update to V3
    Closes Issue #4, #5, #36, #37
    [P-TET-000110-0 Fan Box Base Plate.stl, P-TET-000110-1 Fan Box Base Plate.stl, P-TET-000112-0 Fan Box.stl, P-TET-000112-2 Fan Box.stl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]
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2021-02-26 Rotate body to print orientation
    [P-TET-000104-3 M12 Controller Body.stl]
2021-02-26 adjusting for print orientation
    [P-TET-000100-1 M12 Controller Knob.stl, P-TET-000103-1 M12 Controller Plate.stl, P-TET-000104-0 M12 Light Pipe Clip.stl]
2021-03-06 Transformed to set print orientation
    [P-TET-000112-2 Fan Box.stl, P-TET-000116-1 Fan Box UniFrameCover.stl]
2021-03-06 part numbers and orientations for mask
    [FitMaskClip.stl, FitMaskHoneycombCap.stl, FitMaskMount.stl, LRG_facefitter_V1-6-1-Inner-Ring.STL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]
2021-03-06 Add in dxfs and update drawings
    Added dxf files for the gaskets and updated drawings with new part numbers
    [P-TET-000111-1 Fan Box Gasket.dxf, P-TET-000114-0 Fan Gasket.dxf, P-TET-000115-0 Filter Gasket.dxf, P-TET-000117-0 Funnel Gasket.dxf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]
2021-03-08 Fan Box redesign and MOLLE
    Closing #65
    Closing #6
    #75 WIP
    #66 WIP
    #56 WIP
    #57 WIP
    [P-TET-000110-1 Fan Box Base Plate.stl, P-TET-000110-2 MOLLE Fan Base Plate.stl, P-TET-000112-3 Fan Box.stl, P-TET-000128-0 MOLLE Adapter Short.stl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]
2021-03-08 Part Numbers visible in model after slicing
    Closing #83
    [P-TET-000110-2 MOLLE Fan Base Plate.stl, P-TET-000128-0 MOLLE Adapter Short.stl, P-TET-000129-0 MOLLE Adapter Long.stl]
2021-03-08 Create P-TET-000116-1 UniFrame Filter Cover.stl
    #78 WIP
    [P-TET-000116-1 UniFrame Filter Cover.stl]
2021-03-08 Correcting Labeling in branch
    [P-TET-000116-1 UniFrame Filter Cover.stl, P-TET-000116-2 UniFrame Filter Cover.stl]
2021-03-29 Create P-TET-000117-1 Funnel Gasket.dxf
    Closing #108
    [P-TET-000117-1 Funnel Gasket.dxf]
2021-04-02 STL Upload
    Closing #106, #105, #104, #103, #102, #97, #96, #76, #53, #93
    [P-TET-000100-1_M12_Controller_Knob.stl, P-TET-000102-1 M12 Controller Lid.stl, P-TET-000103-1 M12 Controller Plate.stl, P-TET-000104-0 M12 Light Pipe Clip.stl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]
2021-04-03 Delete P-TET-000100-1_M12_Controller_Knob.stl
    Addressing @mechatroniks-git comment
    [P-TET-000100-1_M12_Controller_Knob.stl]
2021-04-04 Gasket Upload
    New Gasket files
    [P-TET-000111-2_Base_Gasket.dxf, P-TET-000114-1_Fan_Gasket.dxf, P-TET-000115-1_Filter_Gasket.dxf, P-TET-000117-1 Funnel Gasket.dxf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]
2021-04-05 Create P-TET-000112-4_Fan_Outlet.stl
    Add Fan Outlet STL
    [P-TET-000112-4_Fan_Outlet.stl]
2021-04-07 Fixed Bevel on filter housing
    [P-TET-000116-3_Filter_Housing_Louver.stl, P-TET-000116-4_Filter_Housing_Louver.stl]
2021-04-08 Changed MOLLE adapters to match v5 box
    [P-TET-000128-0 MOLLE Adapter Short.stl, P-TET-000128-1_MOLLE_Adapter_Short.stl, P-TET-000129-0 MOLLE Adapter Long.stl, P-TET-000129-1_MOLLE_Adapter_Large.stl]
2021-04-10 Corrected PN for Fan Outlet
    [P-TET-000113-4_Fan_Outlet.stl]
2021-04-17 v6 upload
    [P-TET-000110-3_MOLLE_Base_Plate.stl, P-TET-000110-4_MOLLE_Base_Plate.stl, P-TET-000112-4_Fan_Box.stl, P-TET-000112-5_Fan_Box.stl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]
2021-04-19 New Cover System
    [P-TET-000116-5-Filter_Housing.stl, P-TET-000116-6_Filter_Housing_Lower.stl, P-TET-000133-0_Weather_Cover.stl, P-TET-000133-1_Weather_Cover_Flared.stl]
2021-04-23 New stls
    [P-TET-000112-5_Fan_Box.stl, P-TET-000116-6_Filter_Housing_Lower.stl, P-TET-000133-1_Weather_Cover_Flared.stl]
2021-04-24 Orientation Fix
    [P-TET-000116-6_Filter_Housing_Lower.stl, P-TET-000133-1_Weather_Cover_Flared.stl]
2021-04-24 Corrected Naming Convention
    [P-TET-000100-1_M12_Controller_Knob.stl, P-TET-000131-1_M12_Board_Housing.stl, P-TET-000132-1_M12 Battery Housing.stl, P-TET-000132-1_M12_Battery_Housing.stl]
2021-05-08 New Mask Stem with hose retaining bump
    [P-TET-000130-1 Mask Stem.stl]
2021-05-10 Updating masks to the new models, adding in medium and small
    [P-TET-000120-1 Large Mask.stl]
2021-05-12 Fixed numbering and connection edge
    [P-TET-000131-1_M12_Board_Housing.stl, P-TET-000132-1_M12_Battery_Housing.stl]
2021-05-13 removing the correct file
    [P-TET-000130-0 Mask Stem.stl]
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2021-08-10 New STLs for 96mm fan
    [Fan Box.stl, Fan Outlet.stl, Filter Housing.stl, Latch.stl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]
2021-08-18 Update Test STLs
    [Base Gasket.dxf, Clip.stl, Fan Box.stl, Fan Gasket.dxf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]
2021-08-23 Update Clip.stl
    Rotated clip for correct print orientation.
    [Clip.stl]
2021-08-25 Update Filter Housing.stl
    [Filter Housing.stl]
2021-09-01 Part Number Update
    [P-TET-000110-5_MOLLE_Plate.stl, P-TET-000112-6_Fan_Box.stl, P-TET-000113-5_Fan_Outlet.stl, P-TET-000116-7_Filter_Housing.stl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]
2021-09-01 Reorganized to Correct folders
    [P-TET-000110-4_MOLLE_Base_Plate.stl, P-TET-000110-5_MOLLE_Plate.stl, P-TET-000112-5_Fan_Box.stl, P-TET-000112-6_Fan_Box.stl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]
2021-09-01 Gasket Updated
    [P-TET-000111-2_Base_Gasket.dxf, P-TET-000111-3_Base_Gasket.dxf, P-TET-000114-1_Fan_Gasket.dxf, P-TET-000114-2_Fan_Gasket.dxf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]
2021-09-01 Flip Print orientation
    [P-TET-000112-6_Fan_Box.stl]
2021-09-05 This commit adds in parts that were somehow lost in previous updates, the MOLLE adapters and the mask gasket. It also updates the gitignore to ignore 3mf and gcode files so those don't get accidental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
    [P-TET-000128-0 MOLLE Adapter Short.stl, P-TET-000129-0 MOLLE Adapter Long.stl]
2021-09-13 Clip add Drawing Update
    [P-TET-000139-0_Clip.stl]
2021-09-13 Create P-TET-000121-1_Mask Gasket.dxf
    [P-TET-000121-1_Mask Gasket.dxf]
2021-09-13 restoring the clip
    [P-TET-000139-0_Clip.stl]
2021-10-04 10/4 Upload
    [P-TET-000110-5_MOLLE_Plate.stl, P-TET-000110-6_MOLLE_Plate.stl, P-TET-000111-3_Base_Gasket.dxf, P-TET-000112-6_Fan_Box.stl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]
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2021-11-05 STL Fixes and MOLLE Adapters
    [P-TET-000112-8_Fan_Box.stl, P-TET-000116-9_Filter_Housing.stl, P-TET-000128-2_MOLLE_Adapter_Short.stl, P-TET-000129-2_MOLLE_Adapter_Long.stl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]
2021-11-06 STL Orientation fix
    [P-TET-000112-7_Fan_Box.stl, P-TET-000112-8_Fan_Box.stl, P-TET-000116-8_Filter_Housing.stl, P-TET-000116-9_Filter_Housing.stl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]
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2022-06-12 addresses issue #209 by rearranging directories to make a bit more logical sense.
    [P-TET-000110-6_MOLLE_Plate.stl, P-TET-000112-8_Fan_Box.stl, P-TET-000113-6S_Fan_Outlet_22mm.stl, P-TET-000116-9_Filter_Housing.stl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]
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2022-06-20 Fixing the commit history to remove the Fan Outlet Interface and getting things ready for Darryl to merge his most recent work.
    [P-TET-000140_MOLLE_Base.stl, P-TET-000141_Filter_Interface.stl, P-TET-000142_Filter_Frame.stl, P-TET-000143_Weather_Guard.stl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]
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2023-02-13 Closes #227 by enabling filter swaps without full rebuilds of the box. Was built on stream on Feb 5th 2023.
    [P-TET-000140_MOLLE_Base.stl, P-TET-000141_Filter_Interface.stl, P-TET-000142_Filter_Frame.stl, P-TET-000143_Weather_Guard.stl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]
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
